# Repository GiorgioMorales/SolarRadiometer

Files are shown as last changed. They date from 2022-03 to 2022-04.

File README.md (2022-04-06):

# SolarRadiometer

The aim of this project is to design, calibrate, and validate a simple low-cost sun radiometer.
We follow the method proposed by Forrest Mims [1] which consists of using a light-emitting
diode (LED) as a low-cost detector and optical filter. The LED acts as a photovoltaic (PV)
detector whose short-circuit current (photocurrent) is proportional to the Sun’s irradiance.
This current and, thus, the voltage it generates are amplified by a transimpedace amplifier as shown below [2]:

Fig. 1.
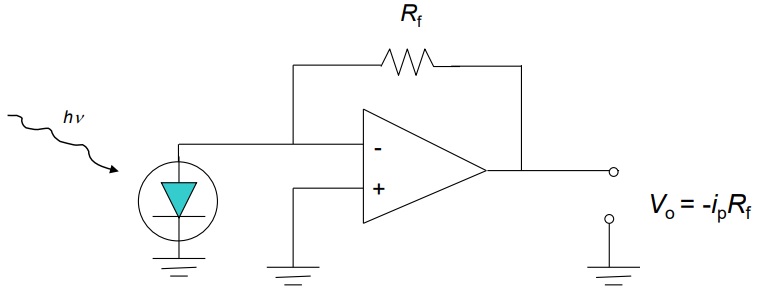
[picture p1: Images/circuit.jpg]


## Device Specifications

The architecture of the proposed system was designed in Solidworks and consists of two
degrees of freedom, as shown in Fig. 2. The tube of this system is designed to house an
LED diode that is used as our sensor. The length of the tube allows the sensor to have
a narrow aperture angle of 3° approximately in order to measure direct radiation only and
avoid the interference of diffused radiation [3]. The LED acts as a PV detector and its short-
circuit current is amplified by an operational amplifier (LM324) using a feedback resistor
Rf = 4M Ω. The amplified signal (voltage) is automatically read by an Arduino UNO. The
amplifier circuit uses a voltage source of ±9V while the servomotors are powered with a
separate voltage source of 5V . The implemented device is shown in Fig. 3. Note that Fig. 3
shows that a red LED was used for initial experiments; however, a green LED (520nm) was
used to collect the data used in this report.

Fig. 2.
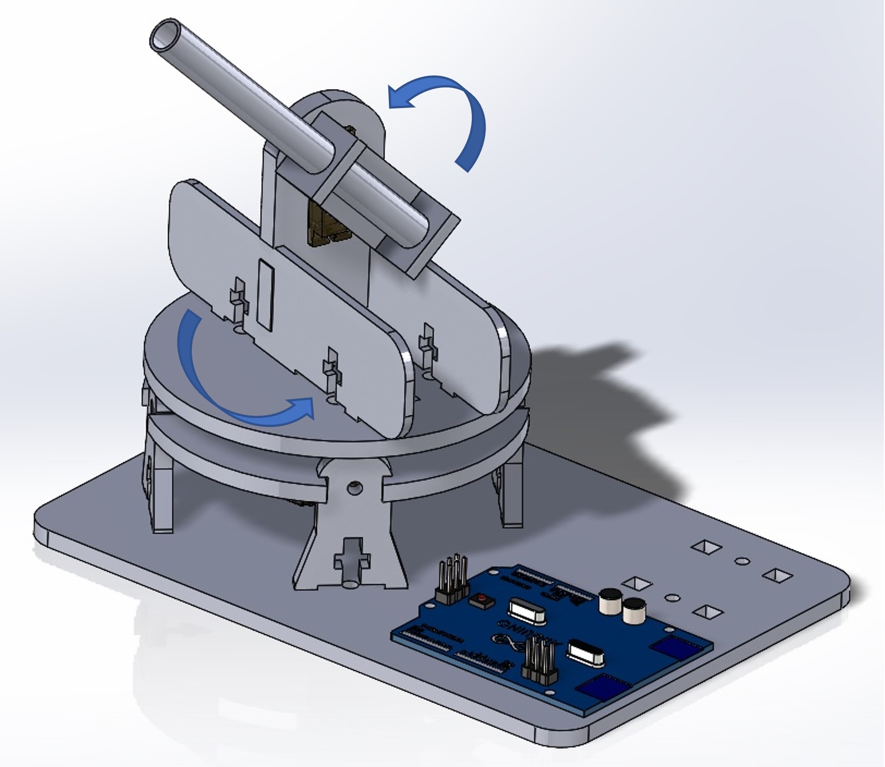
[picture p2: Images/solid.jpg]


Fig. 3.
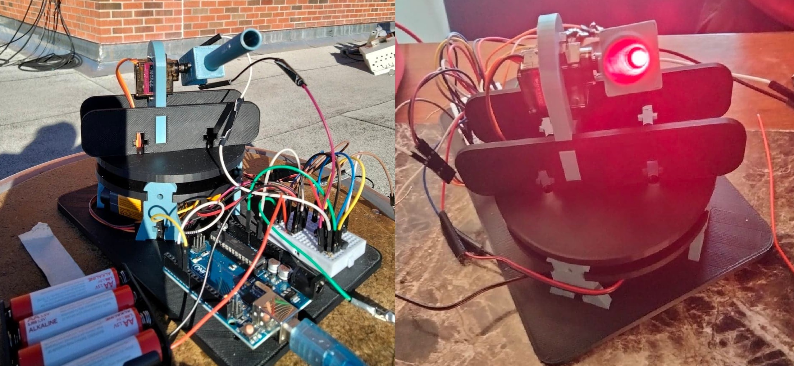
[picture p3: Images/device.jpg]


Fig. 4.
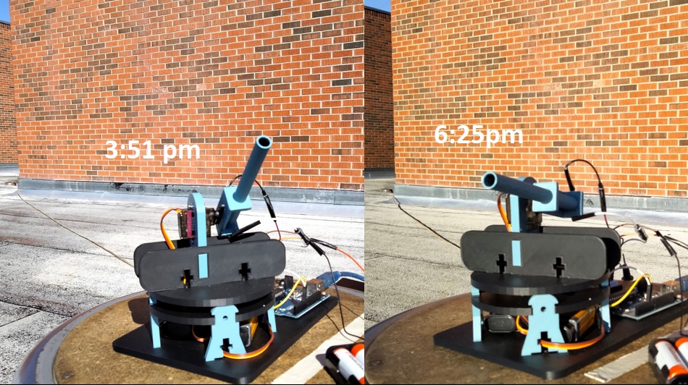
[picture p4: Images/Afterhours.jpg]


The position of the tube is controlled by two servomotors, whose angles are calculated by
the Arduino. More specifically, the purpose of the Arduino program is to align the tube
with the position of the Sun thorough the day; that is, it calculates the Sun’s azimuth and
zenith angles constantly. 

## Results

An example of the data collected is shown in Fig. 5. From this, we obtained the Langley plot shown in Fig. 6.

Fig. 5.


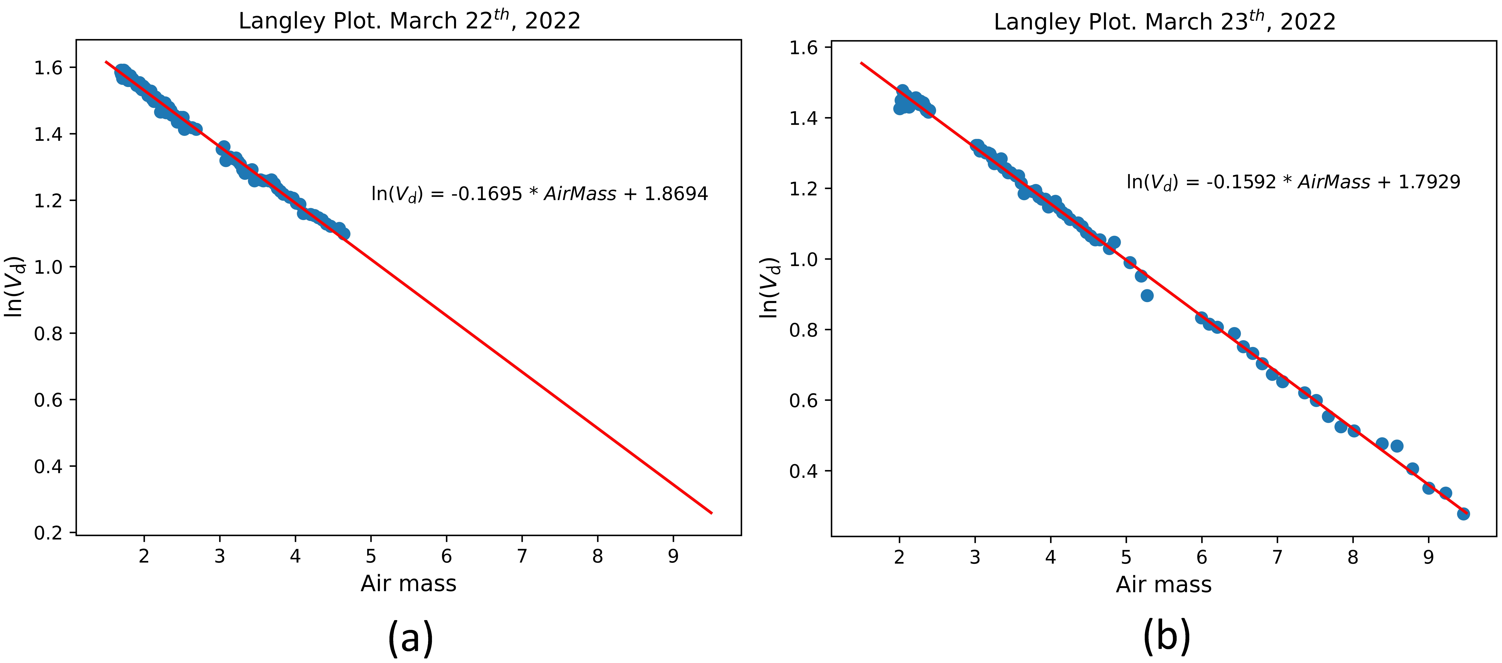
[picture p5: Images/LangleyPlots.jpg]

Fig. 6. Langley plots fitted using data from (a) March 22 and (b) March 23

## Usage

This repository contains the following folders and scripts:

* `Read_Solar.py`: Python script that reads the collected data (.CSV files from the `data` folder) and generates the Langley plots (Fig. 5 and 6).        
* `utils.py`: Python script that contains the functions used to calculate the zenith angle, distance from Sun to Earth, air mass correction, etc.
* `Arduino\SolarRadiometer.ino`: Arduino program that controls the servomotors and stores the data automatically thorough the day.
* `Hardware_Solidworks\`: Folder that contains the Solidworks files of the structure of the device. The subfolder `Files ready for printing` contains the files that can be directly 3D-printed. The design of the moving base was adapted from https://github.com/BrownDogGadgets/SolarTracker

## References
[1] Forrest M. Mims. Sun photometer with light-emitting diodes as spectrally selective de-
tectors. Appl. Opt., 31(33):6965–6967, Nov 1992

[2] Joseph Shaw. Lecture notes in remote sensing systems, EELE 583 - Spring 2022, Montana
State University.

[3] Glenn E. Shaw. Sun photometry. Bulletin of the American Meteorological Society, 64(1):4
– 10, 1983

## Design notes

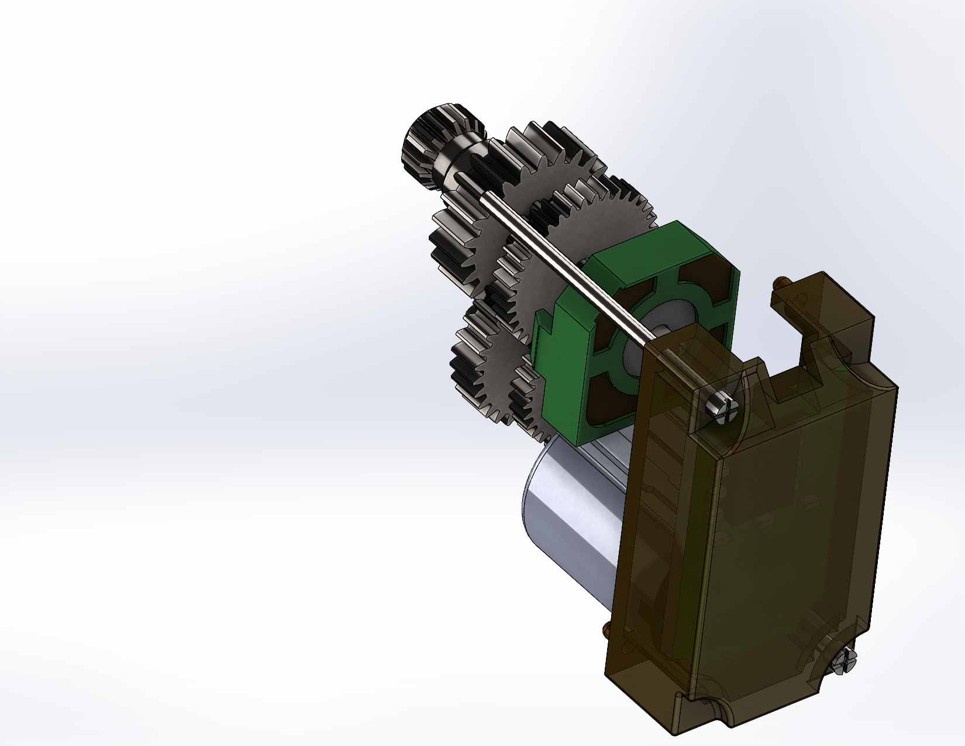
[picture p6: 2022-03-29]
Hardware_Solidworks/servomotor-mg90s-1/MG90S_5.PNG

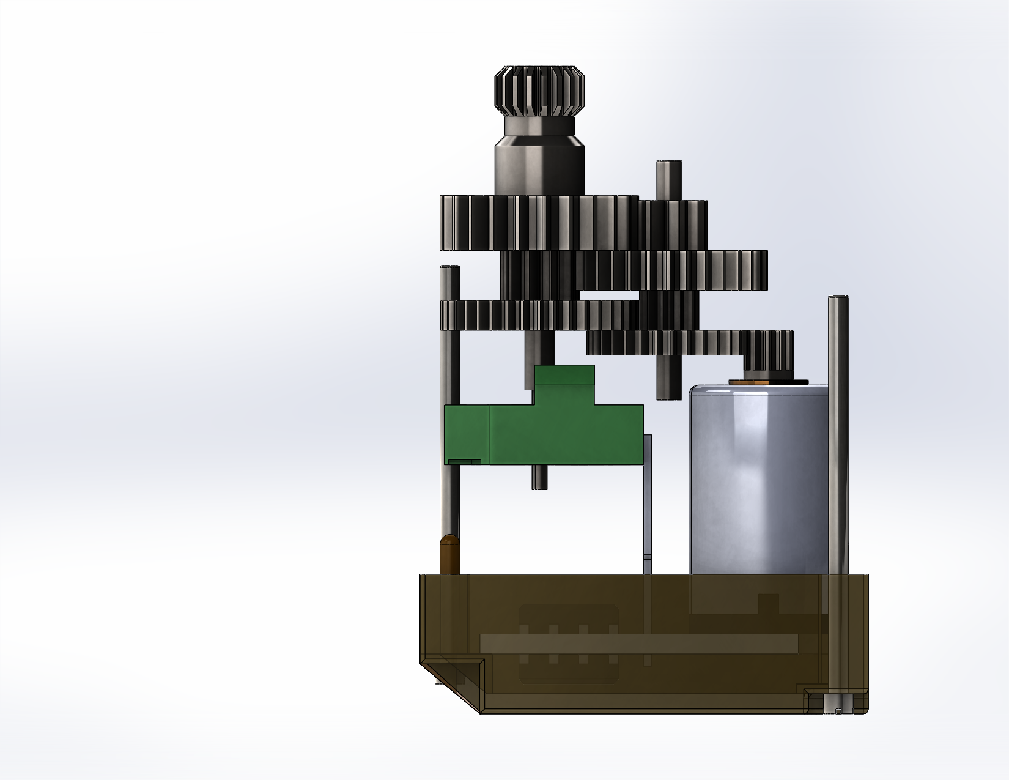
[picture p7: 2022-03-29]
Hardware_Solidworks/servomotor-mg90s-1/MG90S_4.PNG

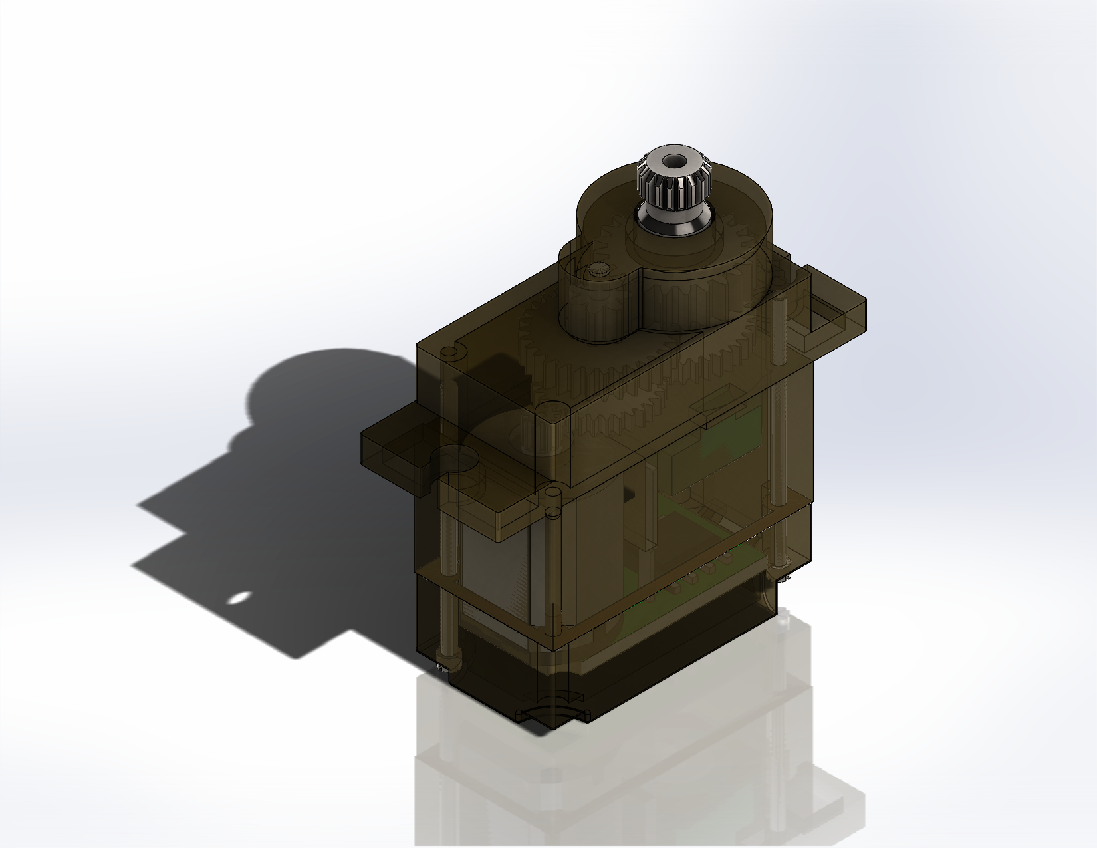
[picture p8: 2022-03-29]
Hardware_Solidworks/servomotor-mg90s-1/MG90S_1.PNG

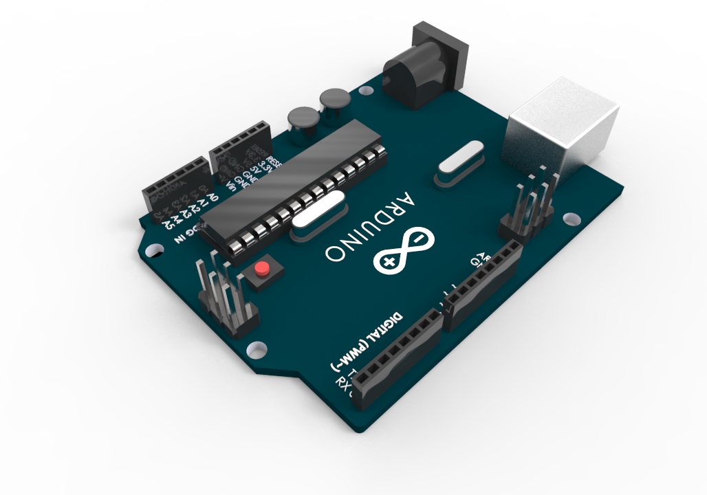
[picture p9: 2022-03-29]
Hardware_Solidworks/arduino-uno-r3-3.snapshot.1/Arduino R3 UNO/Renderings/untitled.21.jpg

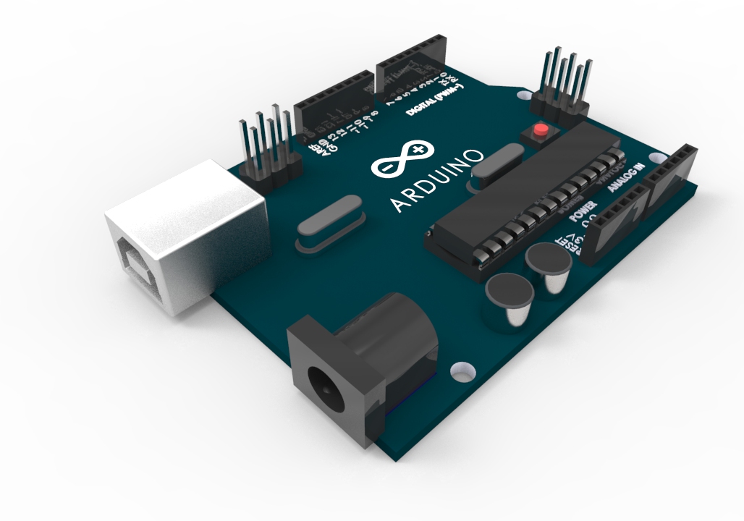
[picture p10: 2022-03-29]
Hardware_Solidworks/arduino-uno-r3-3.snapshot.1/Arduino R3 UNO/Renderings/untitled.19.jpg

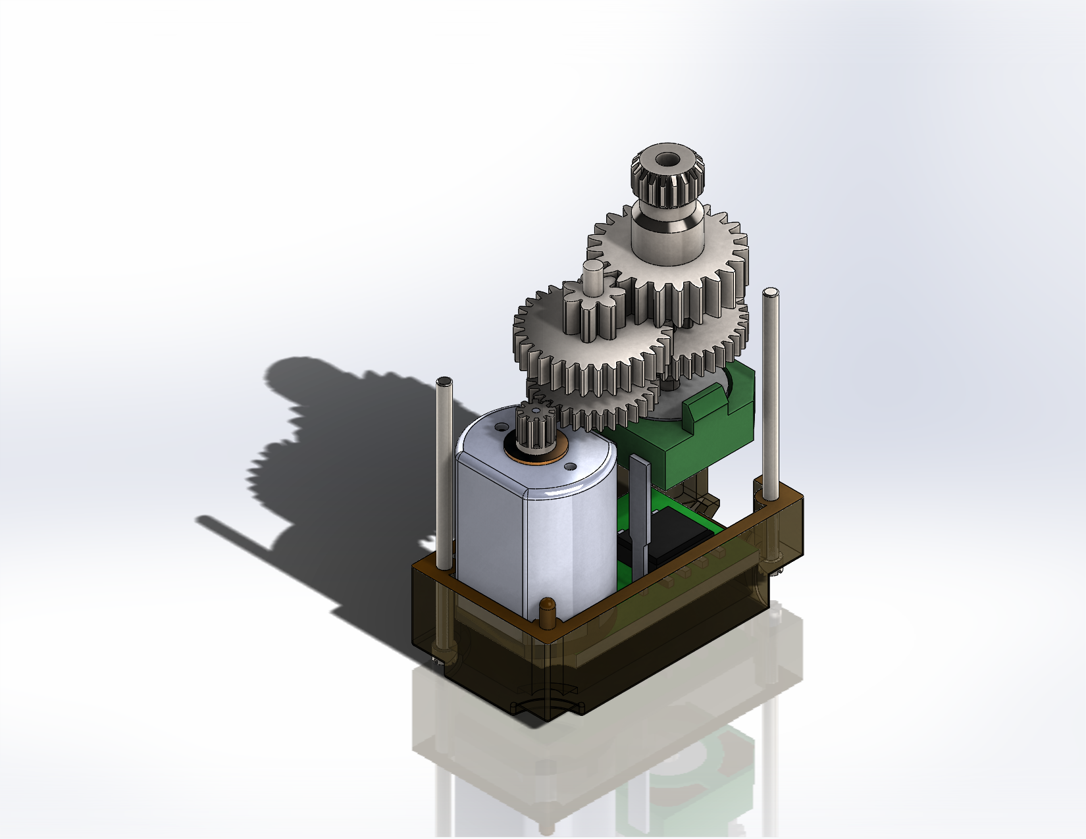
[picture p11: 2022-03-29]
Hardware_Solidworks/servomotor-mg90s-1/MG90S_3.PNG

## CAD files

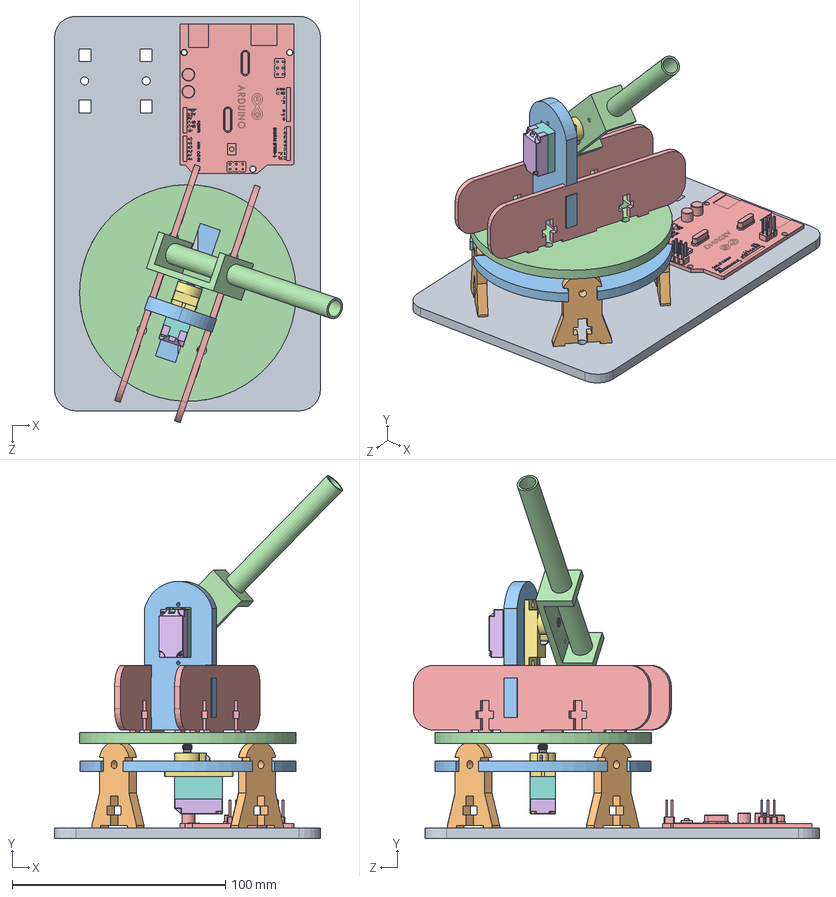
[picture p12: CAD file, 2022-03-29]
Hardware_Solidworks/Assem1.SLDASM
135.1 x 170.2 x 190.5 mm
Base
Column x 4
Disc1
Disc2
ColumnServo2 x 2
Motor_Body2 x 12
gear3 x 2
gear1 x 2
gear2 x 2
Motor_Body x 2
cilinder2 x 2
cilinder1 x 2
ColumnServo
holder
Arduino board

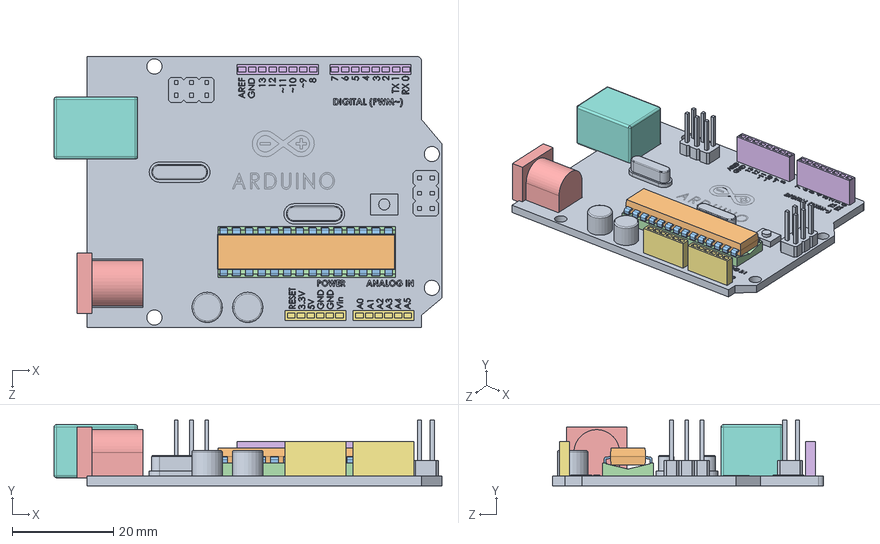
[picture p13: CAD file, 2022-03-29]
Hardware_Solidworks/arduino-uno-r3-3.snapshot.1/Arduino R3 UNO/uno.SLDASM
76.5 x 13.0 x 53.5 mm
Arduino board
IC body
IC pin x 28
IC socket
Jack Socket
pin x 2
pin2 x 2
USB socket

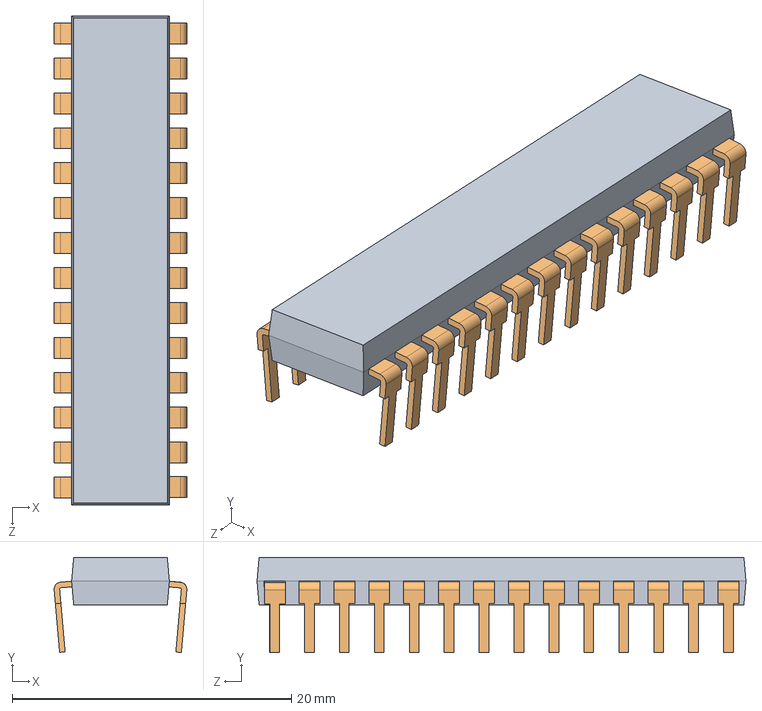
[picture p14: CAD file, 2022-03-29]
Hardware_Solidworks/arduino-uno-r3-3.snapshot.1/Arduino R3 UNO/IC.SLDASM
9.50 x 6.80 x 35.0 mm
IC body
IC pin x 28

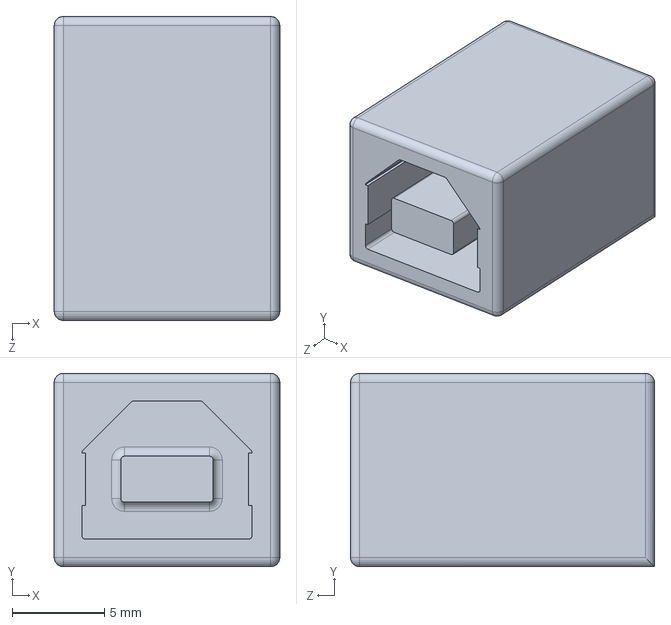
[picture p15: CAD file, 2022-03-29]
Hardware_Solidworks/arduino-uno-r3-3.snapshot.1/Arduino R3 UNO/USB socket.SLDPRT
12.2 x 10.5 x 16.5 mm

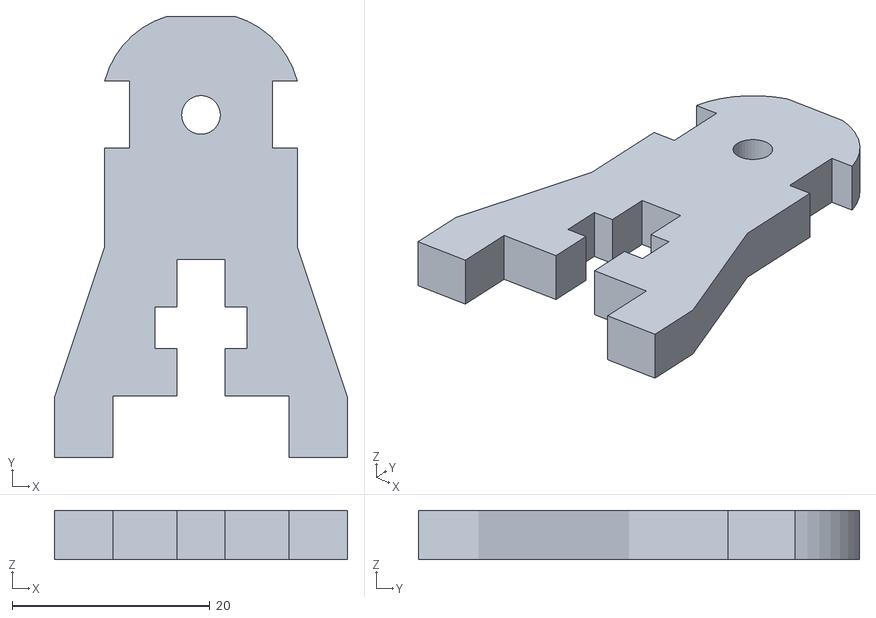
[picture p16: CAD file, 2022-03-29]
Hardware_Solidworks/Files ready for printing/Column.STL
29.7 x 44.6 x 5.00

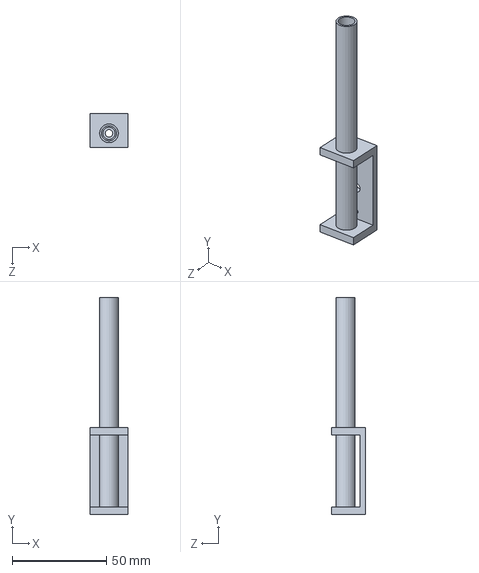
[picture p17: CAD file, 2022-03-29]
Hardware_Solidworks/holder.SLDPRT
20.0 x 115.0 x 18.0 mm

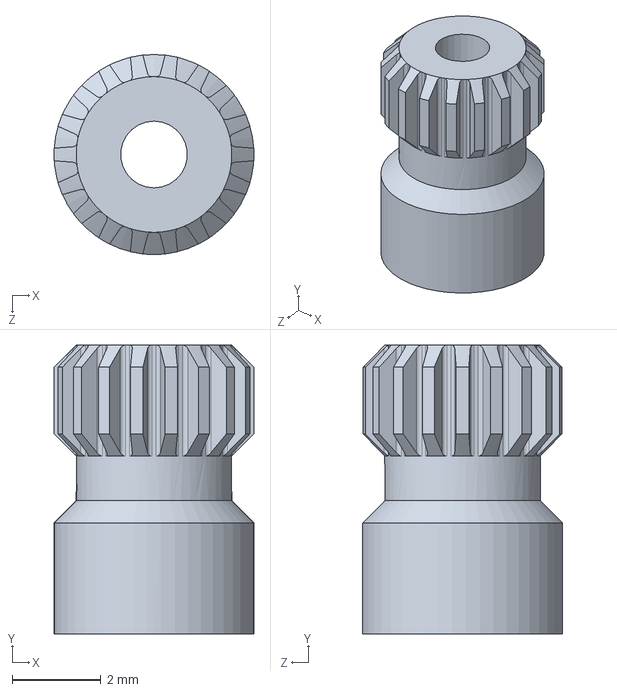
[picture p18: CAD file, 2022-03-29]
Hardware_Solidworks/servomotor-mg90s-1/Part4.SLDPRT
4.50 x 6.50 x 4.50 mm

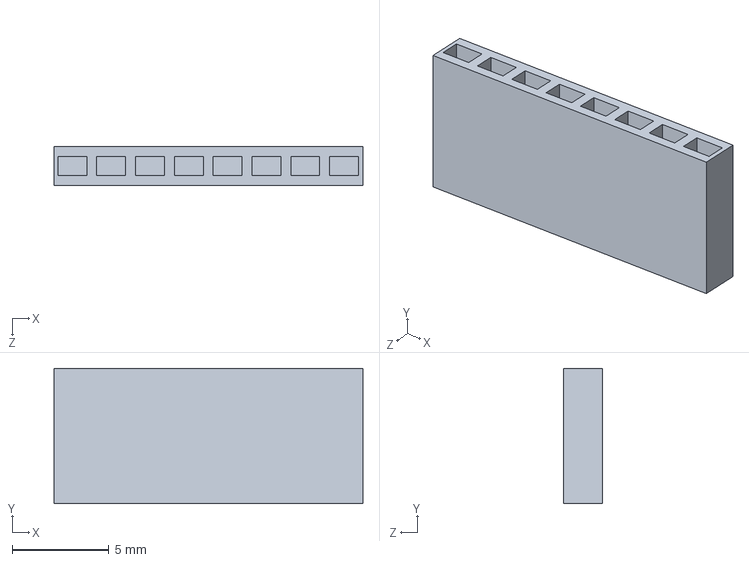
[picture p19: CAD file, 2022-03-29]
Hardware_Solidworks/arduino-uno-r3-3.snapshot.1/Arduino R3 UNO/pin.SLDPRT
16.0 x 7.00 x 2.00 mm

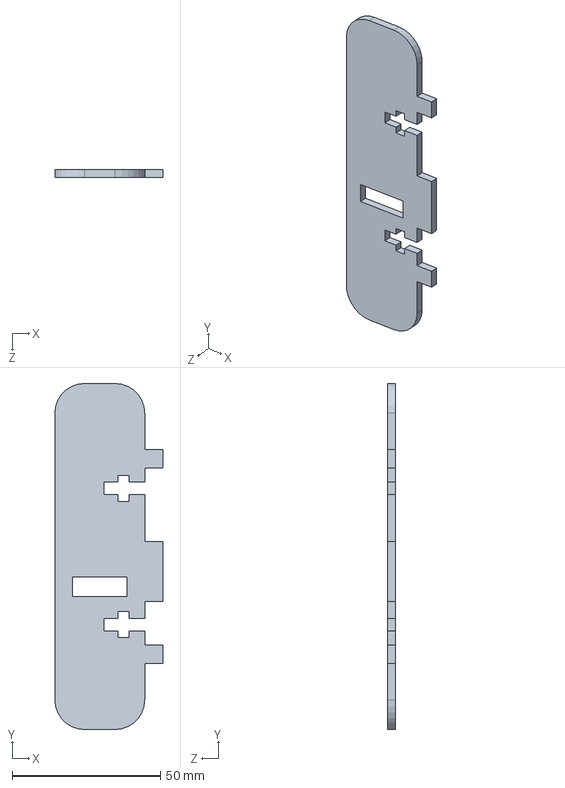
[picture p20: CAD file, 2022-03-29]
Hardware_Solidworks/ColumnServo2.SLDPRT
36.6 x 116.8 x 2.80 mm

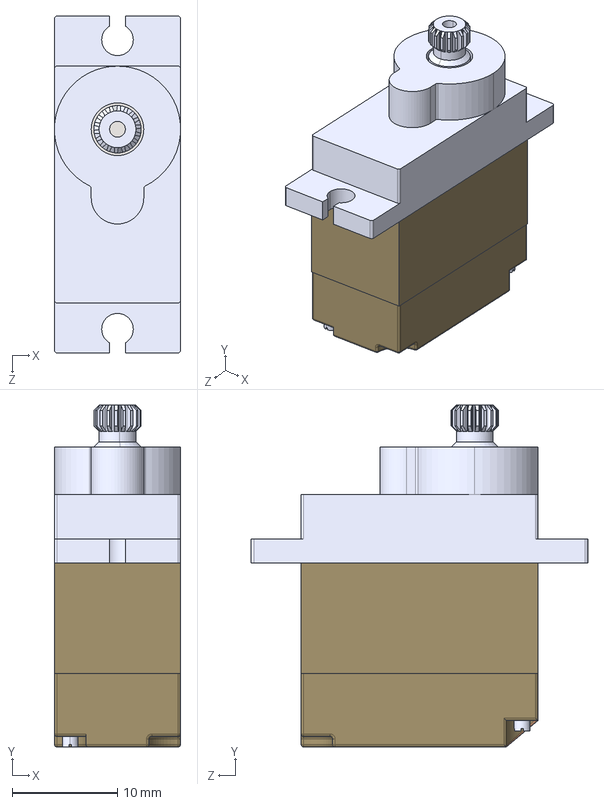
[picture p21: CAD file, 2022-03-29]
Hardware_Solidworks/servomotor-mg90s-1/MG90S.STEP
12.0 x 32.5 x 32.0 mm
spur gear_iso_ISO - Spur gear 0.25M 38T 20PA 1.5FW ---S38A75H50L1.5N
spur gear_iso_ISO - Spur gear 0.3M 31T 20PA 2FW ---S31A75H50L1.25N
spur gear_iso_ISO - Spur gear 0.4M 23T 20PA 2.75FW ---S23A75H50L1.5N
spur gear_iso_ISO - Spur gear 0.25M 31T 20PA 1.25FW ---S31A75H50L1.25N
spur gear_iso_ISO - Spur gear 0.25M 10T 20PA 2FW ---S10A75H50L1.25N
gear3
gear1
gear2
Motor_Body
Motor_Body2
cilinder2
cilinder1

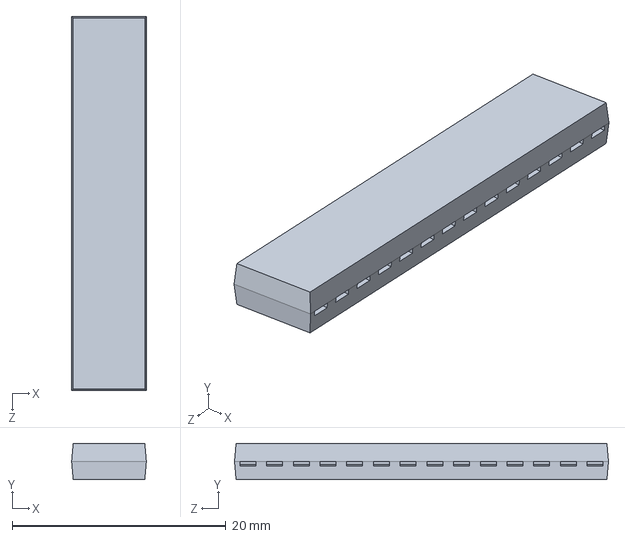
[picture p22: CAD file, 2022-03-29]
Hardware_Solidworks/arduino-uno-r3-3.snapshot.1/Arduino R3 UNO/IC body.SLDPRT
7.00 x 3.40 x 35.0 mm

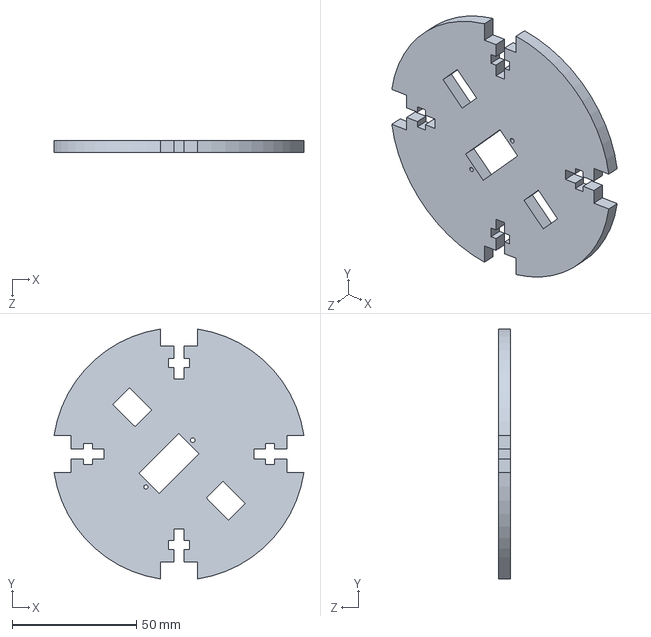
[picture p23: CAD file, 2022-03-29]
Hardware_Solidworks/Disc1.SLDPRT
100.5 x 100.5 x 5.00 mm

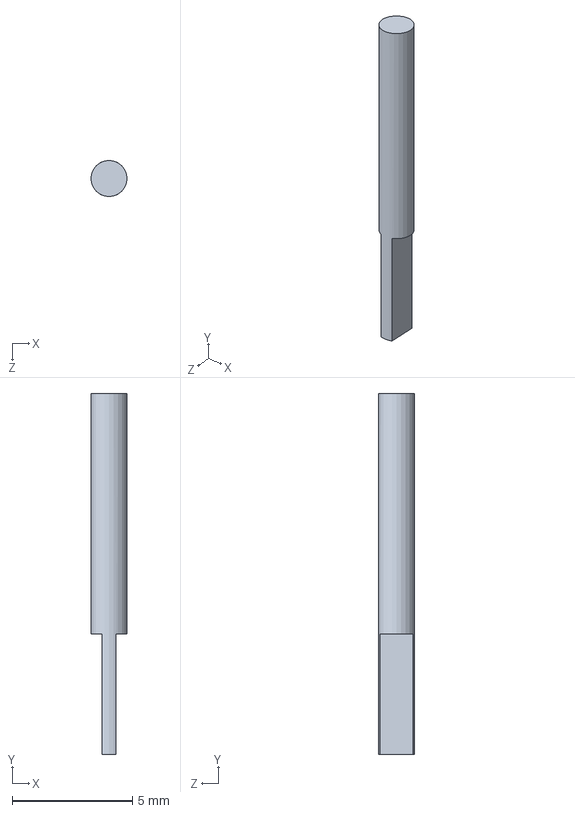
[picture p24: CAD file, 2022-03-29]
Hardware_Solidworks/servomotor-mg90s-1/cilinder2.SLDPRT
1.50 x 15.0 x 1.50 mm

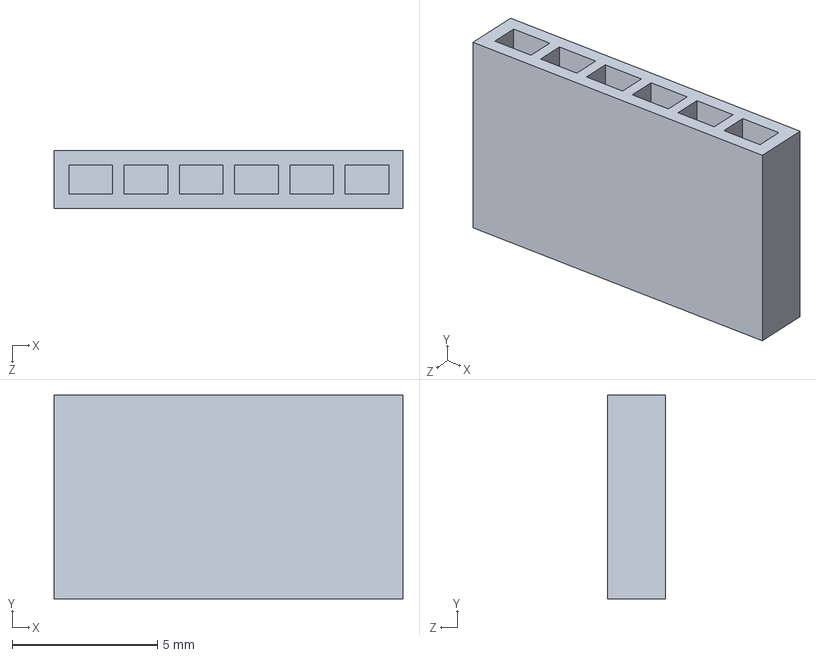
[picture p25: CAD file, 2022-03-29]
Hardware_Solidworks/arduino-uno-r3-3.snapshot.1/Arduino R3 UNO/pin2.SLDPRT
12.0 x 7.00 x 2.00 mm

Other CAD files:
Hardware_Solidworks/Files ready for printing/holder.STL
Hardware_Solidworks/Files ready for printing/Disc1.STL
Hardware_Solidworks/Files ready for printing/Base.STL
Hardware_Solidworks/servomotor-mg90s-1/gear3.SLDPRT
Hardware_Solidworks/Base.SLDPRT
Hardware_Solidworks/Column.SLDPRT
Hardware_Solidworks/ColumnServo.SLDPRT
Hardware_Solidworks/Disc2.SLDPRT
Hardware_Solidworks/Files ready for printing/ColumnServo.STL
Hardware_Solidworks/Files ready for printing/ColumnServo2.STL
Hardware_Solidworks/Files ready for printing/Disc2.STL
Hardware_Solidworks/Solar_tracker_solidworks.SLDPRT
Hardware_Solidworks/arduino-uno-r3-3.snapshot.1/Arduino R3 UNO/Arduino board.SLDPRT
Hardware_Solidworks/arduino-uno-r3-3.snapshot.1/Arduino R3 UNO/IC pin.SLDPRT
Hardware_Solidworks/arduino-uno-r3-3.snapshot.1/Arduino R3 UNO/IC socket.SLDPRT
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

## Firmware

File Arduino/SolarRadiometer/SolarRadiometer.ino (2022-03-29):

#include <Servo.h>
#include <C:\Users\w63x712\Documents\MSU Courses\Remote Sensing\SolarRadiometerProject\Arduino\SolarRadiometer\SolarPosition.h>

// Make sure to copy the Time and SolarPosition libraries in the same directory. Modify the line above

// Test positions
SolarPosition Home(45.668305, -111.059107);  // Nelson Story Tower
SolarPosition Cobleigh(45.666596, -111.045824); // Cobleigh Hall Rooftop (Final Test)

// Create a fixed UNIX initial time. 
// IMPORTANT: The initial hour MUST be provided as a reference for Arduino. COMPILE RIGHT BEFORE USING THE CODE.
// Also, align the device to the East or until there is no shadow around the tube. 
int someS = 0;  //second
int someM = 56;  //minute
int someH = 7 + 6; //hour. +6 (MST) to get UTM time
int someD = 23; //day
int someMo = 3; //month
int someY = 2022; //year
tmElements_t someTime = {someS, someM, someH, 0, someD, someMo, CalendarYrToTm(someY) };
time_t initialTime = makeTime(someTime);

// Servo variables
Servo servobase, servoled;
float azimuth, zenith;

// Voltage reader variables
const float arduinoVCC = 5.01;    //Arduino voltage
const int alanogPin = A0;         //the pin connecting the voltage. 
const int inputResolution =1023;  //works with most Arduino boards


void setup() {  
  // Configure servo pins
  servobase.attach(5);
  servoled.attach(6);

  // Set initial servo positions
  servobase.write(0);  // Look EAST
  servoled.write(0);   // Look up (Zenith = 0) 
  
  Serial.begin(9600);
  Serial.println("Initializing Solar Radiometer........");
  delay(500);  

  // set Time clock 
  setTime(initialTime);
  // set the Time library time service as the time provider
  SolarPosition::setTimeProvider(now);

  // Align the tube to the calculated azimuth and zenith angles.
  // Stop here during 20 seconds, during which period you should align the device with the Sun
  // making sure there is no shadow around the tube
  // Calculate solar angle (zenith and azimuth).
  azimuth = 180 - getAzimuth(Cobleigh, initialTime);
  zenith = getZenith(Cobleigh, initialTime);
  // Move servos to the calculated position.
  servobase.write(azimuth);  
  servoled.write(zenith);
  Serial.println(F("You have 20 seconds to align the device with the Sun..."));
  delay(20000);
}

void loop() {
  /*
   * Main loop. Refreshes every minute.
   */

  // Step 1: Calculate solar angle (zenith and azimuth).
  azimuth = 180 - getAzimuth(Home, initialTime);
  zenith = getZenith(Home, initialTime);
  Serial.print(F("The sun was at a zenith of "));
  Serial.print(zenith, 4);
  Serial.print(F(" and an azimuth (servo angle) of "));
  Serial.println(azimuth, 4);
  digitalClockDisplay();

  // Step 2: Move servos to the calculated position.
  Serial.println(F("Moving to corresponding position..."));
  servobase.write(azimuth);  
  servoled.write(zenith);

  // Step 3: Perform grid search around the current position to find the maximum voltage lecture.  
  Serial.println(F("Performing grid search..."));
  float maxV = gridSearch();
  Serial.print("Maximum Average Voltage (V): \t");
  Serial.println(maxV);

  // Step 4: Save voltage measurement in a CSV file.
  // Use Tools->ArduSpreadSheet and save the output.
 
  delay(60000); 

  // Step 5: Update time
  someS = second();  
  someM = minute();  
  someH = hour(); 
  someTime = {someS, someM, someH, 0, someD, someMo, CalendarYrToTm(someY)};
  initialTime = makeTime(someTime);
}


float gridSearch(){
  // Moves the zenith nd azimuth angles of the servo +/-5° searching the maximum voltage lecture
  float Vr;
  float maxV = 0;
  delay(1000);
  for(int ang1 = azimuth - 3; ang1 <= azimuth + 3; ang1 += 1){
    for(int ang2 = zenith - 3; ang2 <= zenith + 3; ang2 += 1){
      // Move to the new position
      servobase.write(ang1);  
      servoled.write(ang2);
      delay(100); // Pause just to ensure stability
      // Read voltage
      Vr = getVoltageAverage();
      // Update maximum voltage if necessary
      if(Vr >= maxV){
        maxV = Vr; 
      }
    }
  }
  // Note: This process takes ~8sec
  return maxV;  
}


float getZenith(SolarPosition Position, time_t time_eval){  
  return 90 - Position.getSolarPosition(time_eval).elevation;  // Convert elevation to zenith
}

float getAzimuth(SolarPosition Position, time_t time_eval){  
  return Position.getSolarPosition(time_eval).azimuth - 90;  // Calculate azimuth and subtract 90° bc the radiometer starts facing East
}


float getVoltageAverage(){
  //Take 10 voltage samples with an interval of 5ms, then calculate the average.
  float voltage = 0; int A0Value;
  for(int i=0; i < 10; i++){
    A0Value = analogRead(alanogPin);
    voltage += A0Value * (arduinoVCC / (float)inputResolution); 
    delay(10);
  }      
  return voltage / 10;
}


void digitalClockDisplay(){
  // Digital clock display of the time
  Serial.print(someH);
  printDigits(someM);
  printDigits(someS);
  Serial.print(" ");
  Serial.print(someD);
  Serial.print(" ");
  Serial.print(someMo);
  Serial.print(" ");
  Serial.print(someY); 
  Serial.println(); 
}

void printDigits(int digits){
  // Utility function for digital clock display: prints preceding colon and leading 0
  Serial.print(":");
  if(digits < 10)
    Serial.print('0');
  Serial.print(digits);
}
